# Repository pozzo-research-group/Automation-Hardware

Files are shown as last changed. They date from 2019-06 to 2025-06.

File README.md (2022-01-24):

# Custom Hardware for Automation
Pozzo Group Custom Automation Hardware. Dimensions are consistent with SLAS standards (slas.org) 

## Purpose
A place to store and share files for custom hardware and labware created for the laboratory automation including use with Opentrons pippetting robot and other tools. 

## Required Components
1. Any files (.stl, .dxf, etc.) necessary to create the hardware (3D printing, machining, laser cutting, etc.) 
2. Any drawings or description that is necessary to define the labware in liquid handling platforms (e.g. [Opentrons](https://support.opentrons.com/en/articles/3136504-creating-custom-labware-definitions))
3. Any additional instructions for printing, loading, or using the hardware



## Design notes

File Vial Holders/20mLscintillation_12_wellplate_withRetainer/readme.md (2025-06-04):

# 12 well 20mL vial holders
                                                                                                                                                                                                                                                            Works with 20mL scintillation vials. Use M3 heat set inserts in the holes on the well plate, and long m3 screws through the lids, to retain the vials in the well plate while withdrawing from septa.

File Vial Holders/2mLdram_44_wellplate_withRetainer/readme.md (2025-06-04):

# 44 well 2mL vial holders

Works with 2mL snap-top dram vials. Use M3 heat set inserts in the holes on the well plate, and long m3 screws through the lids, to retain the vials in the well plate while withdrawing from septa.

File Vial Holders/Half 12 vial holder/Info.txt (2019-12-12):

### Purpose
This holder can be used to hold twelve (12) 20 mL scintillation vials in a single
slot of the OT2 pipetting robot

### Use specifics
In order to make a single holder, two of these .stl files will need to be printed,
they then wedge together in a single slot holder and can hold 12 vials

### Measurements per 1 print
* Height:19.5 mm
* Length:85.87 mm
* Width: 63.85 mm
* Wells: 6
* Well Depth: 17.21 mm
* Well Diameter: 27.85 mm

### Well layout
[[A1 A2 A3 A4],
[B1 B2 B3 B4],
[C1 C2 C3 C4],

### Well Pipetting Order:
[A1, B1, C1, A2, B2, C2, A3, B3, C3, A4, B4, C4]

### Code for loading

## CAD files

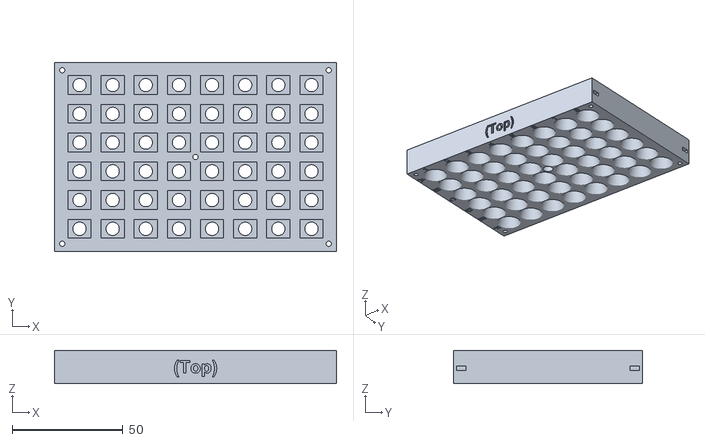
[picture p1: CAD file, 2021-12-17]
Cartridge Sample Holder for SAS Experiments/SAXS-USAXS 48 solid film holder/USAXS solid film holder cartridge v14 part 2.stl
127.5 x 85.5 x 15.0

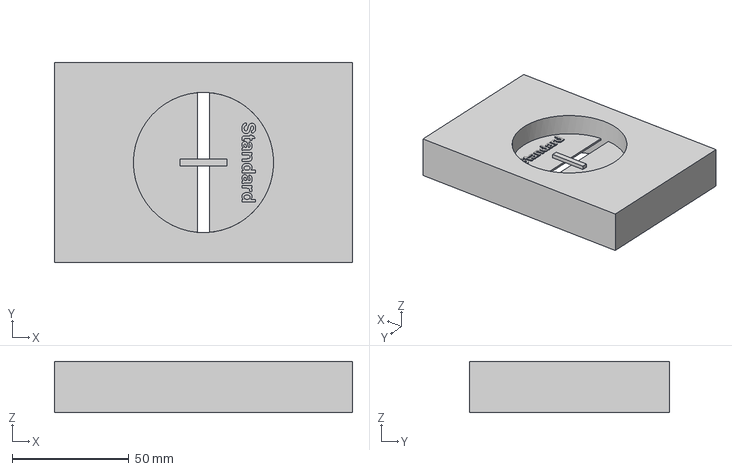
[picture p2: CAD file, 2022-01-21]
Cartridge Sample Holder for SAS Experiments/SAXS-USAXS calibrant holder/USAXS Calibrant Holder.step
127.5 x 85.5 x 22.0 mm

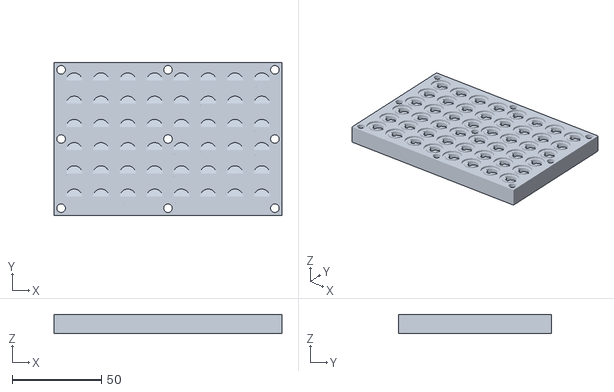
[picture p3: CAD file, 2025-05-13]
Cartridge Sample Holder for SAS Experiments/SAXS-USAXS Liquids 48 well plate holder/Sedimentation_wellplate.stl
127.6 x 85.5 x 10.9

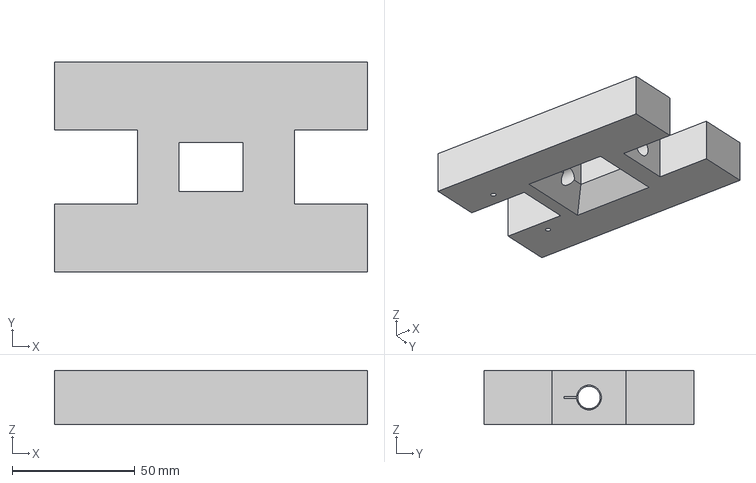
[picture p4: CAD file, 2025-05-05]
Cartridge Sample Holder for SAS Experiments/SAXS-USAXS_AntonPaar_FlowCellHolder/USAXS_flow cell holder v5.step
127.5 x 85.5 x 22.0 mm

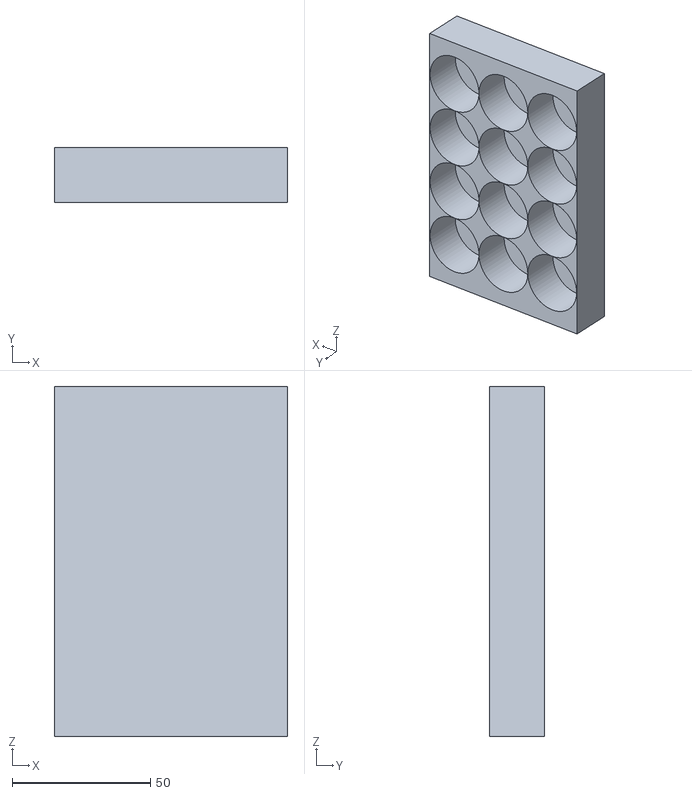
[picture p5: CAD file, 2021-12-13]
Vial Holders/20mlscintillation_12_wellplate_18000ul/20mlscintillation_12_wellplate_18000ul.stl
84.5 x 20.0 x 126.8

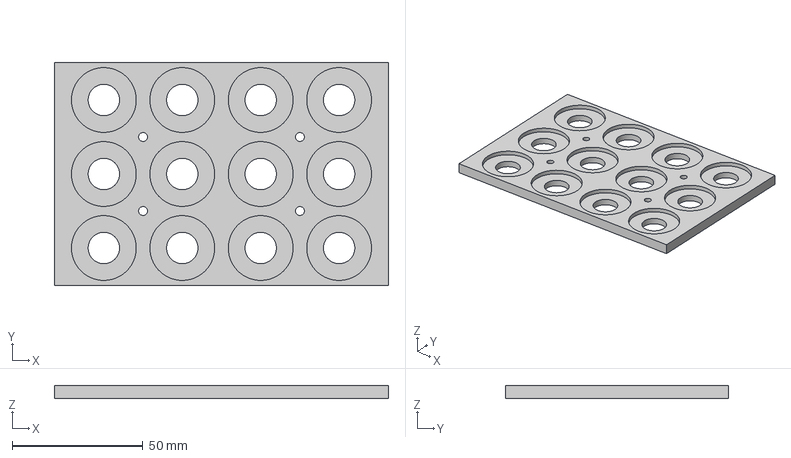
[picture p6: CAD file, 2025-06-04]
Vial Holders/20mLscintillation_12_wellplate_withRetainer/20cc_vial_plate_retainerlid v2.step
127.8 x 85.5 x 5.00 mm

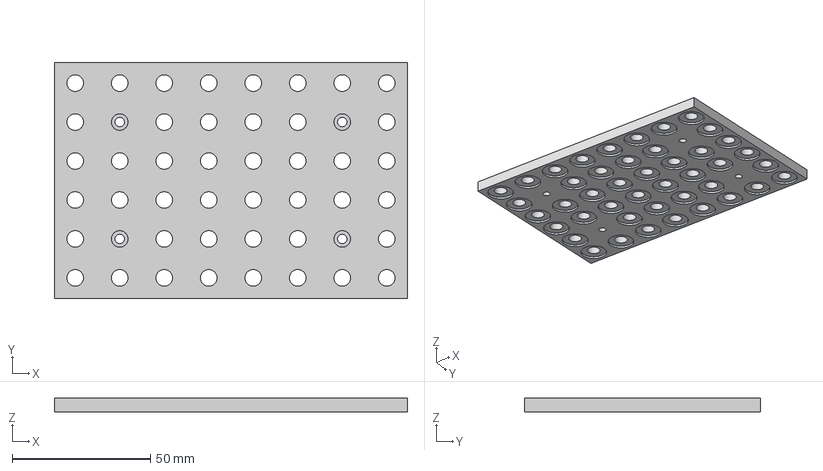
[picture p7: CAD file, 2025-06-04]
Vial Holders/2mLdram_44_wellplate_withRetainer/48_vial_plate_retainerLid v2.step
127.8 x 85.5 x 5.00 mm

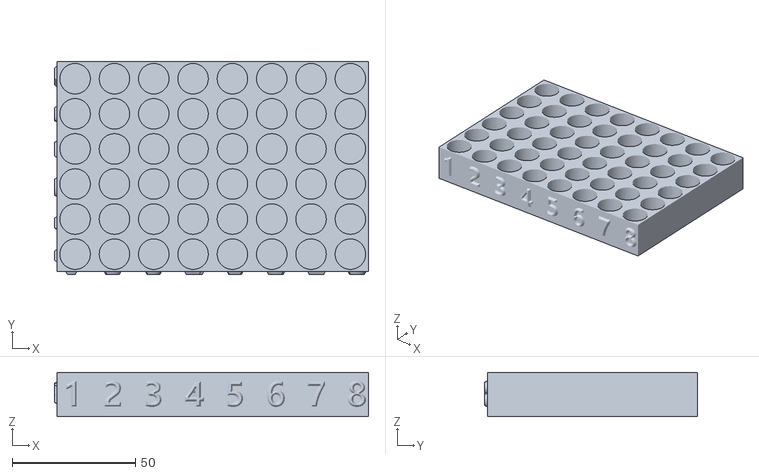
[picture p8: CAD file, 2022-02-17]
Vial Holders/48_well_vial_new_embossed.stl
127.5 x 86.7 x 18.0

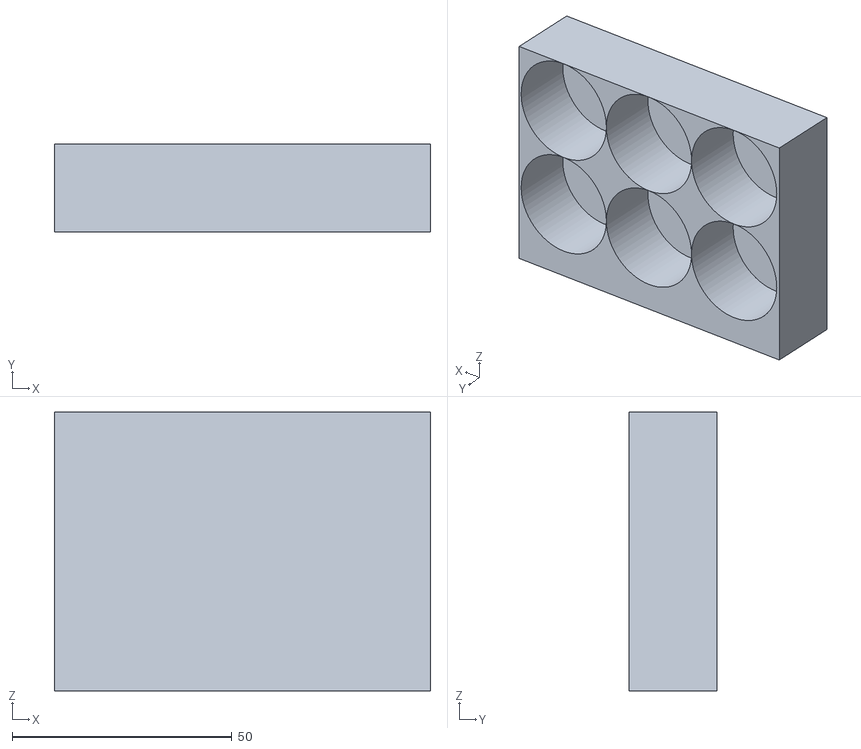
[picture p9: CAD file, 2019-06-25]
Vial Holders/Half 12 vial holder/Half 12 vial holder new.stl
85.5 x 20.0 x 63.4

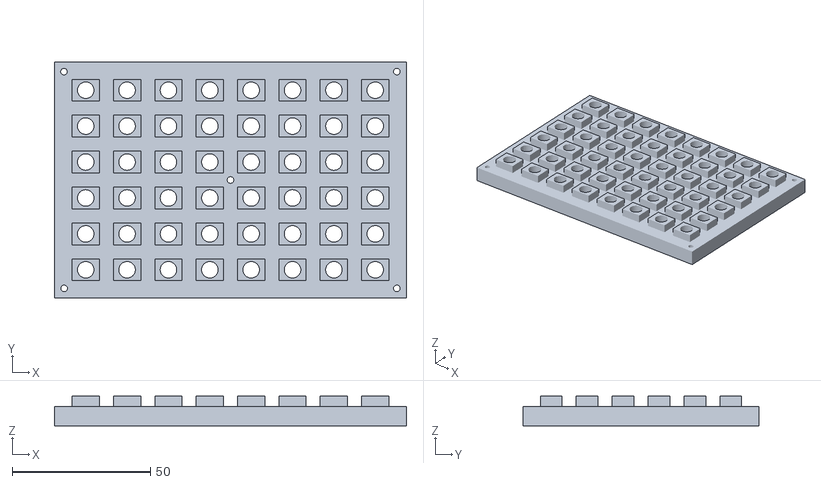
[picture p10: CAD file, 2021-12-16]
Cartridge Sample Holder for SAS Experiments/SAXS-USAXS 48 solid film holder/USAXS solids back (0p3mm gap).stl
127.5 x 85.5 x 10.7

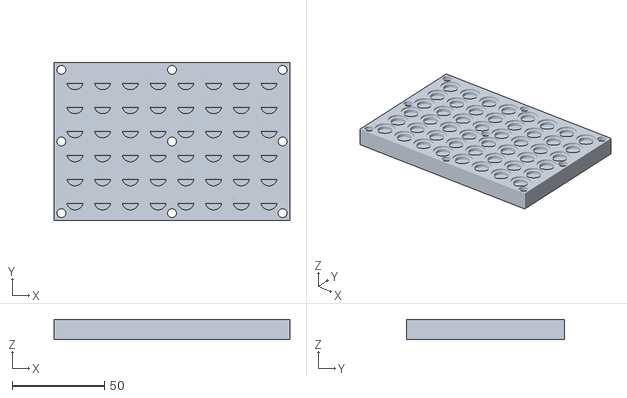
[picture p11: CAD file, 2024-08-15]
Cartridge Sample Holder for SAS Experiments/SAXS-USAXS Liquids 48 well plate holder/SAXS_2mm_sample_thickness - 48 Well (Center).stl
127.6 x 85.5 x 10.9

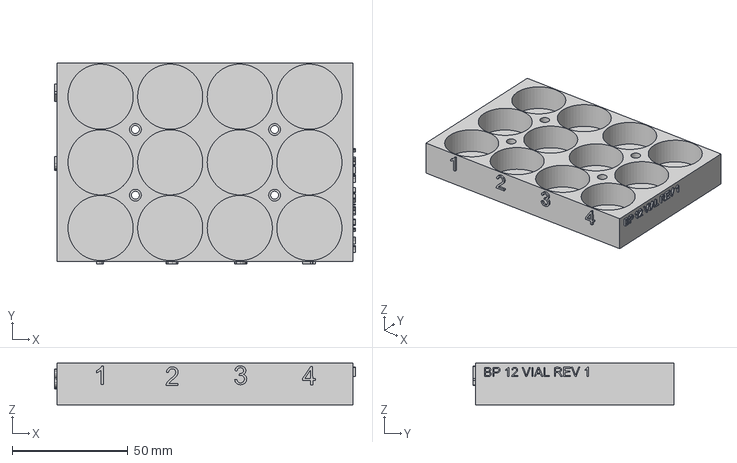
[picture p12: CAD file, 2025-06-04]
Vial Holders/20mLscintillation_12_wellplate_withRetainer/20cc_vial_plate v5.step
129.8 x 86.5 x 18.0 mm

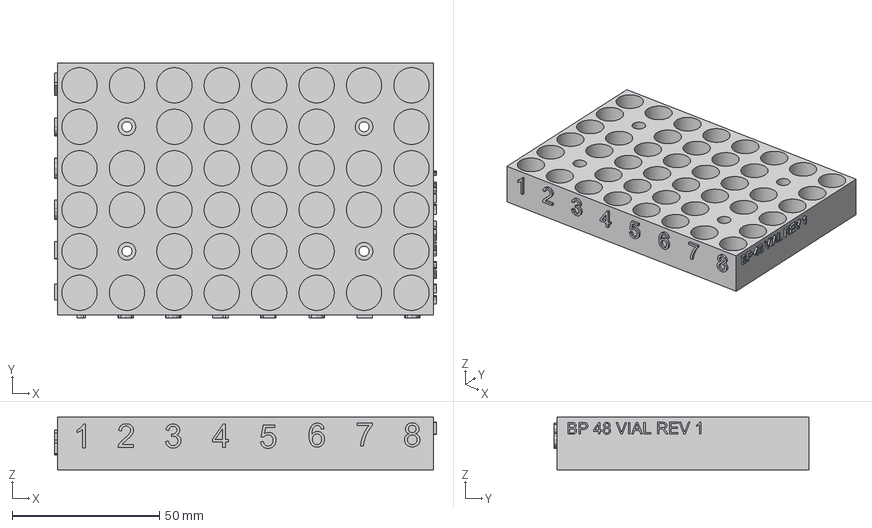
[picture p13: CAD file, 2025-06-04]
Vial Holders/2mLdram_44_wellplate_withRetainer/48_vial_plate v2.step
129.8 x 86.5 x 18.0 mm

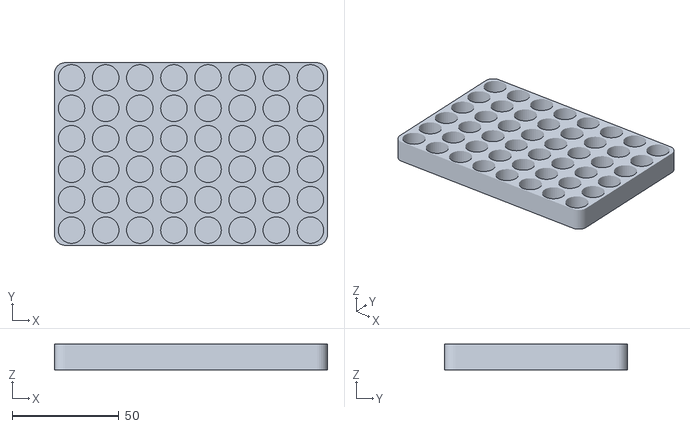
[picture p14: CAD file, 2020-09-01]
Vial Holders/48_well_2ml_vials.stl
127.8 x 85.5 x 12.0

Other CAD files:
Cartridge Sample Holder for SAS Experiments/SAXS-USAXS 48 solid film holder/USAXS solid back (0p8mm gap).stl
Cartridge Sample Holder for SAS Experiments/SAXS-USAXS Liquids 48 well plate holder/Cover plate detector - 48 Well USAXS.step
Cartridge Sample Holder for SAS Experiments/SAXS-USAXS Liquids 48 well plate holder/Cover Plate source - 48 Well USAXS.step
Cartridge Sample Holder for SAS Experiments/SAXS-USAXS Liquids 48 well plate holder/Center - 48 Well Liquids USAXS.step
Cartridge Sample Holder for SAS Experiments/SAXS-USAXS Liquids 48 well plate holder/KaptonWindow.dxf
Cartridge Sample Holder for SAS Experiments/SAXS-USAXS Liquids 48 well plate holder/USAXS liquid side unlabelled.stl
Cartridge Sample Holder for SAS Experiments/SAXS-USAXS Liquids 48 well plate holder/liquids center (aluminum insert).stl
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

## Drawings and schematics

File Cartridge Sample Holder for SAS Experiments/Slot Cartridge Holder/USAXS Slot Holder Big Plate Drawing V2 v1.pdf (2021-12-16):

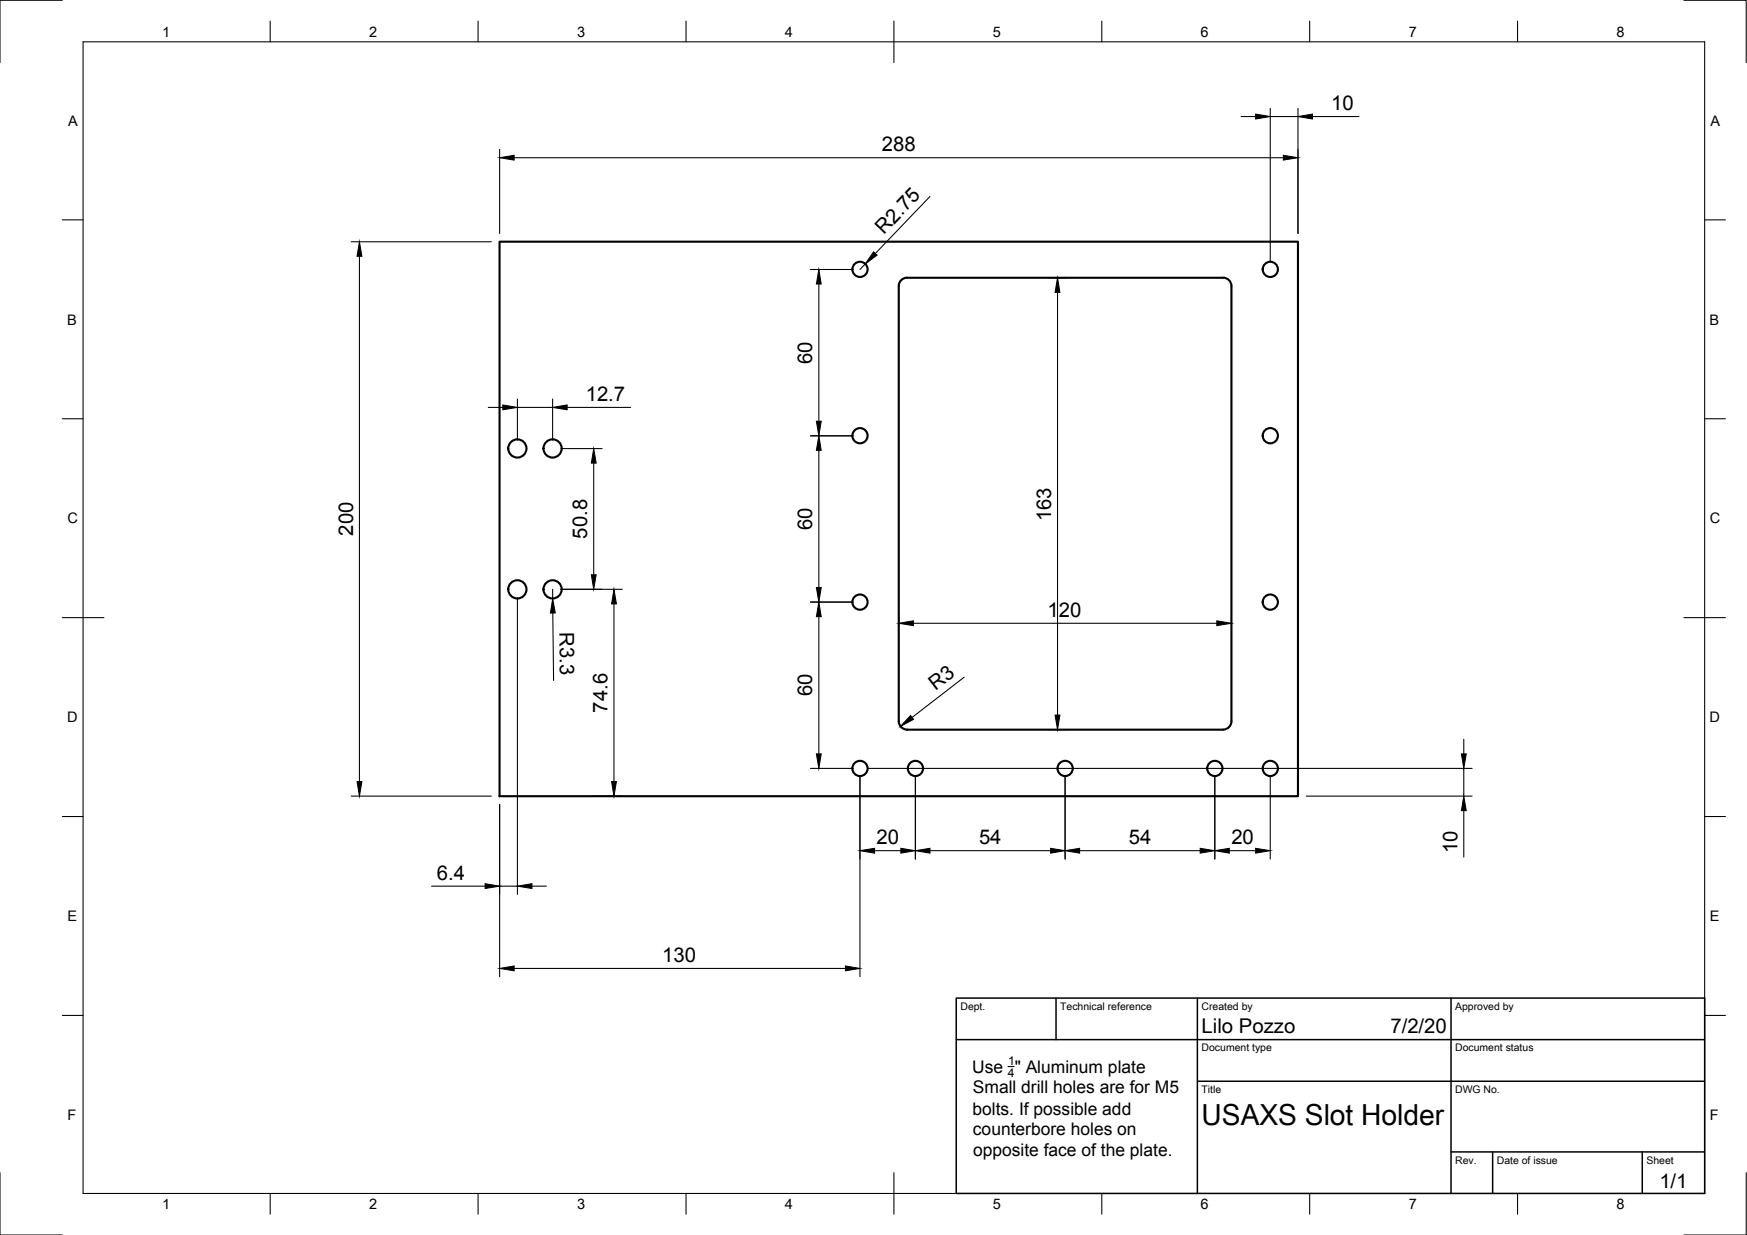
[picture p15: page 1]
Lilo Pozzo 200

Dept. | Technical reference | Created by 7/2/20 | Approved by

Use 1 " Aluminum plate 4 Small drill holes are for M5 bolts. If possible add counterbore holes on opposite face of the plate. | | Document type | Document status

Title USAXS Slot Holder | DWG No.

Rev. | Date of issue | Sheet 1/1

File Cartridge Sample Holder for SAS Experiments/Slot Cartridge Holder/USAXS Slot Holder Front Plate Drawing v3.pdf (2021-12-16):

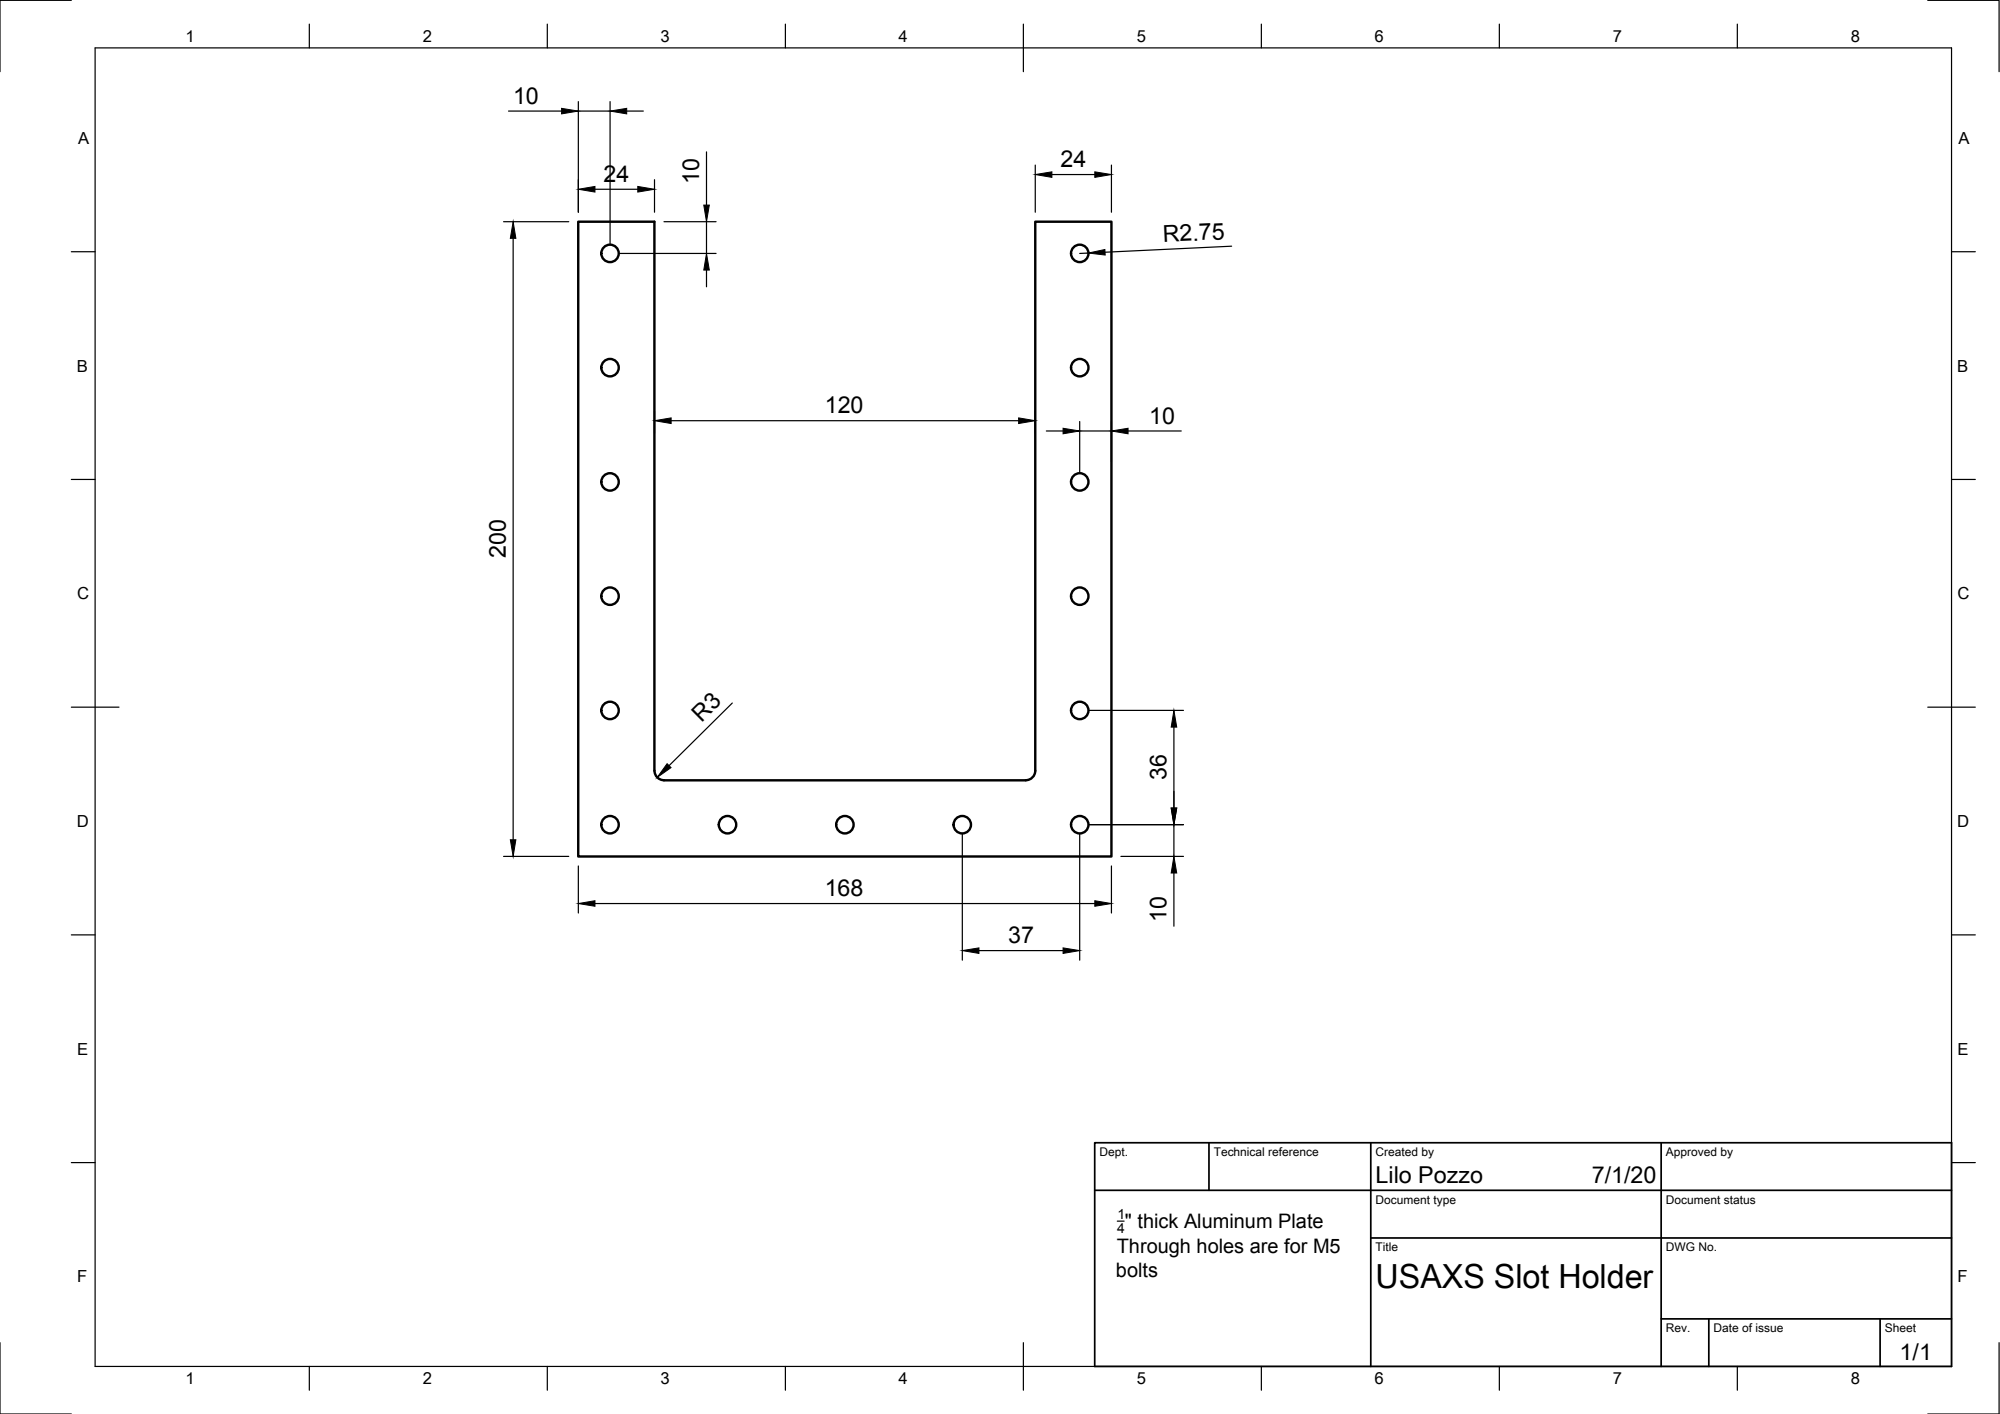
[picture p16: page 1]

Dept. | Technical reference | Created by Lilo Pozzo 7/1/20 | Approved by

1/4" thick Aluminum Plate Through holes are for M5 bolts | | Document type | Document status

Title USAXS Slot Holder | DWG No.

Rev. | Date of issue | Sheet 1/1

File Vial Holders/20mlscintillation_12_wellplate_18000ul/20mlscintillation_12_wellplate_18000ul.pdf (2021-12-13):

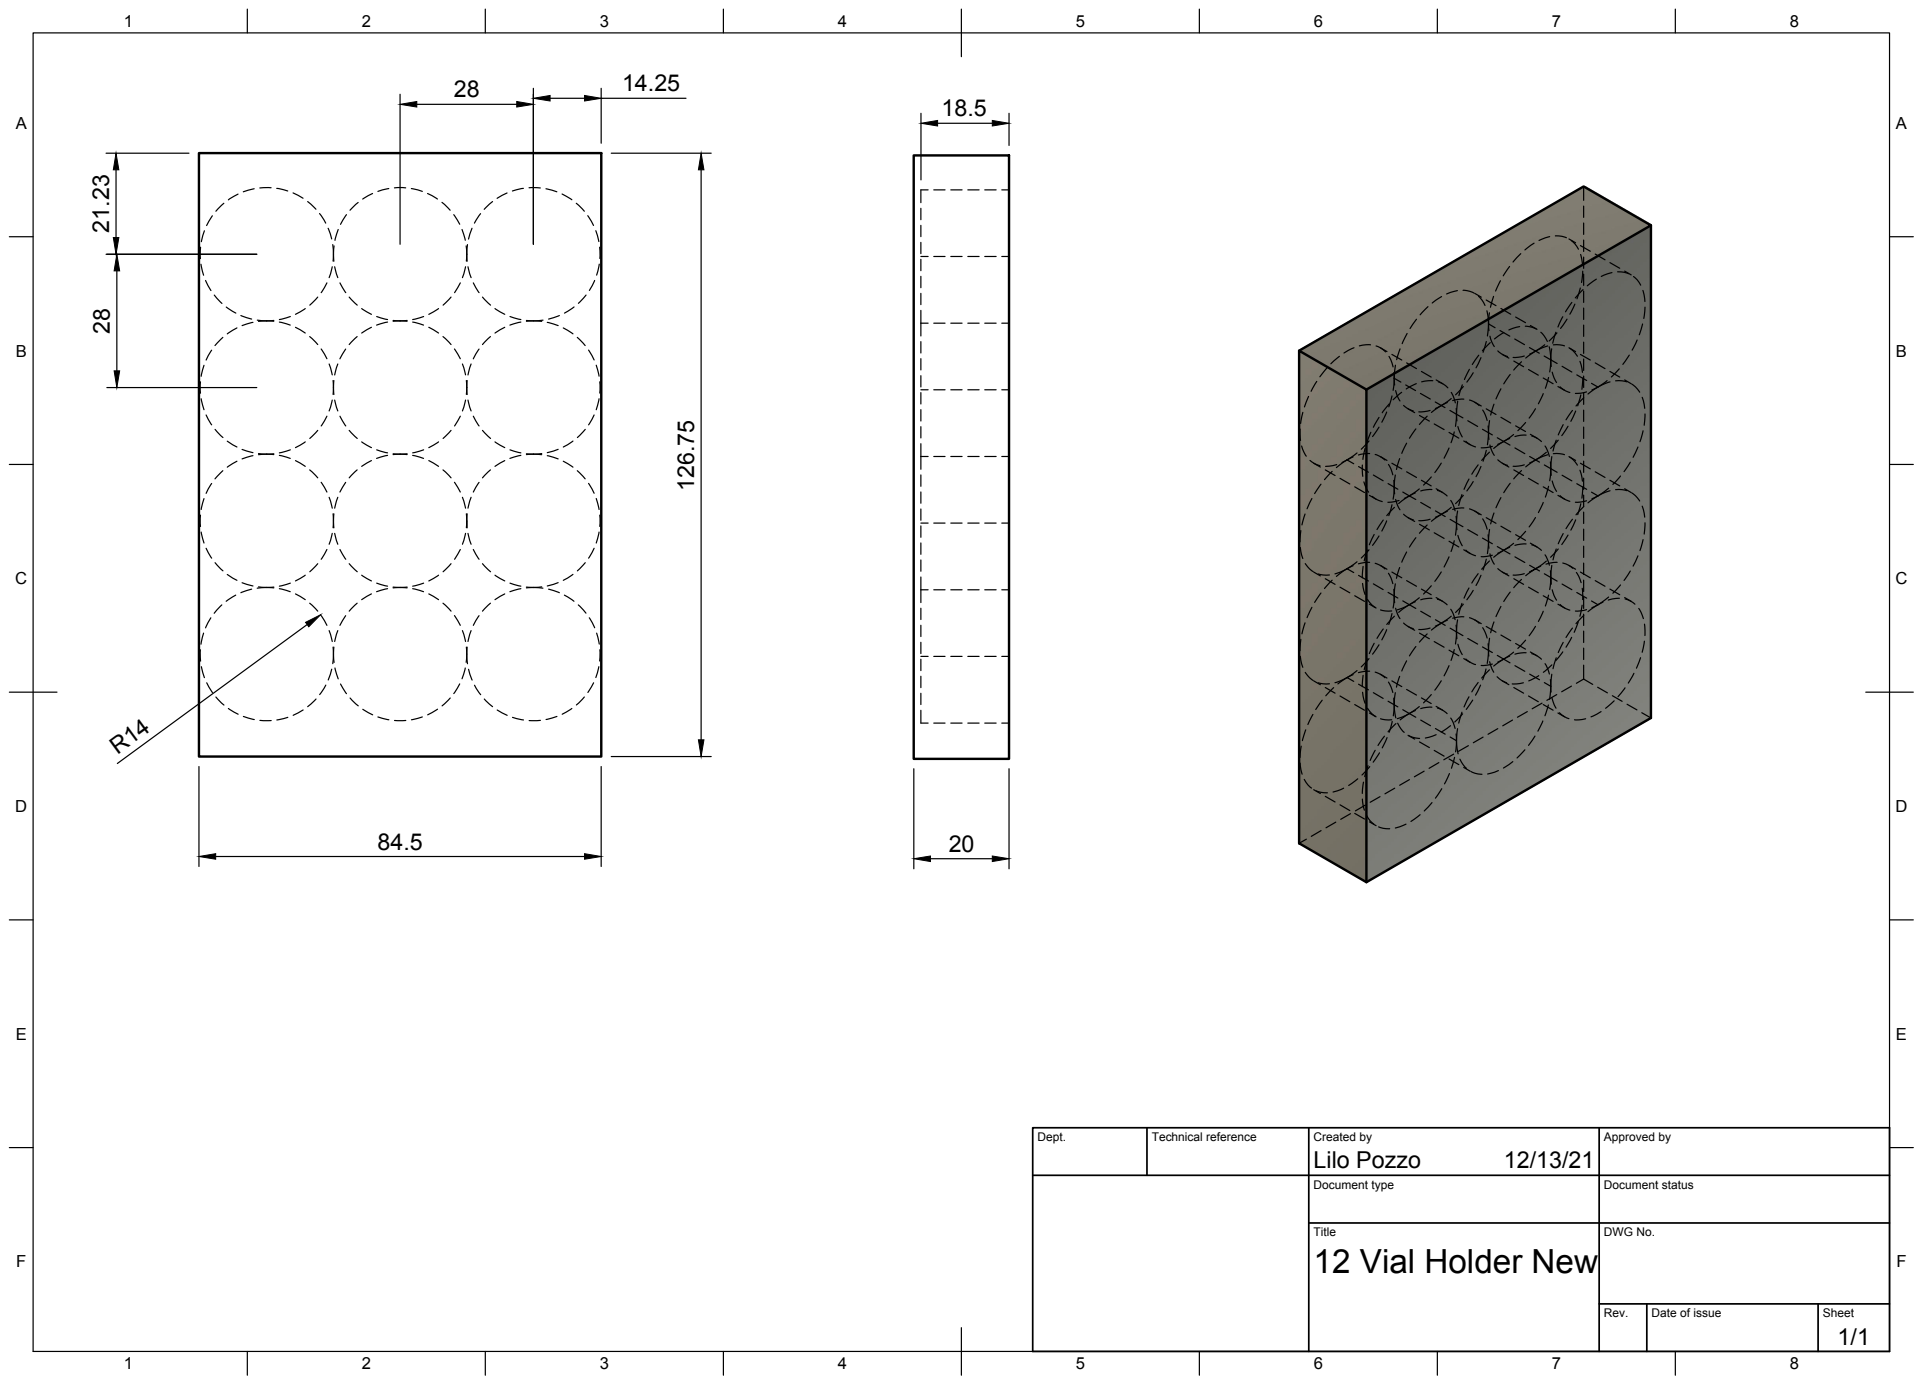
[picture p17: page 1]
Title; DWG No.; Rev.; Date of issue; Sheet

Dept. | Technical reference | Created by Lilo Pozzo 12/13/21 | Approved by

Document type | Document status

12 Vial Holder New

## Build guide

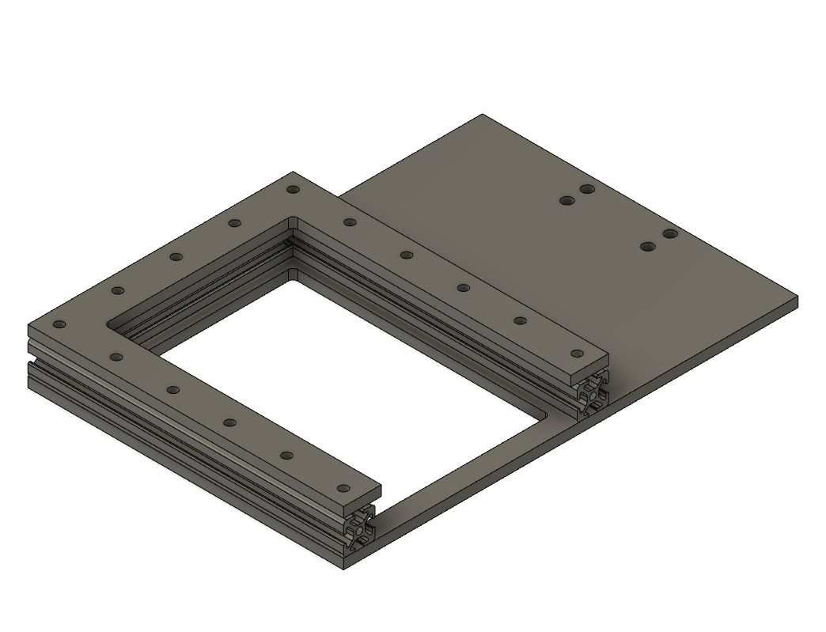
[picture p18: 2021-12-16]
Cartridge Sample Holder for SAS Experiments/Slot Cartridge Holder/USAXS Slot Holder Assembly v6 2.png

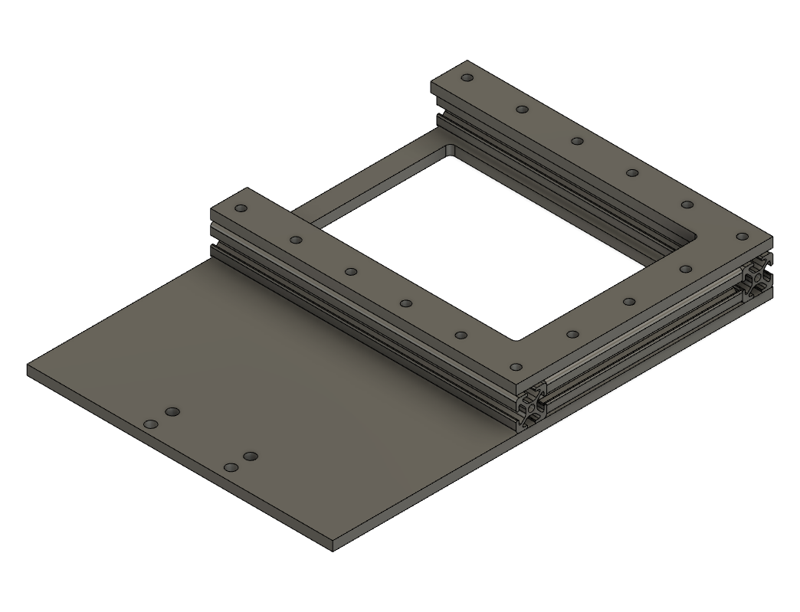
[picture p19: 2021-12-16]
Cartridge Sample Holder for SAS Experiments/Slot Cartridge Holder/USAXS Slot Holder Assembly v6.png

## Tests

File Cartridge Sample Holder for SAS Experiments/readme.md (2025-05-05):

A variety of sample holder designs for use with SAXS cartridge stages. The Slot Cartridge Holder is a cartridge stage adapter for use at APS USAXS 12-ID-E to mount a cartridge cell to the instrument's sample stage. It is constructed out of aluminum plate and extrusion. Use it to mount the solid, liquid, or flow cell holders. The calibrant is used to hold a standard. Tape the standard onto the side of the holder with the 'nub' sticking out.

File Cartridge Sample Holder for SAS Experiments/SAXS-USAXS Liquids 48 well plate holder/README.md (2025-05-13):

# List of Materials

| Supplier      | Material and Dimensions                      | Catalog Number                 | Part Name              | Qty. |
|---------------|----------------------------------------------|--------------------------------|------------------------|------|
| Formlabs      | Clear or Gray                                | RS-F2-GPCL-04 or RS-F2-GPGR-04 | Center piece/main body | 1    |
| McMaster-Carr | Aluminum                                     | 9140T109                       | Cover plate source     | 1    |
| McMaster-Carr | Aluminum                                     | 9140T109                       | Cover plate detector   | 1    |
| McMaster-Carr | Kapton (0.0010" thick)                       | 2271K401                       | Windows                | 2    |
| McMaster-Carr | Buna-N or EPDM (1.5 mm wide, 9 mm ID)        | 9262K126 or 1289N319           | O-rings                | 96   |
| McMaster-Carr | Stainless steel M3 (8 mm Long, 0.5 mm Pitch) | 90666A104                      | Screws                 | 18   |
| MiSUMi        | Brass Cadmium-Free (M3x0.5 mm)               | FB-305580                      | Threaded insert        | 9    |
| McMaster-Carr | Moisture-Resistant Polyester Film (Mylar)    | 8567K102                       | Windows                | 1    |

# Assembly Instructions

For the USAXS 48-wellplate (1cm sample thickness) 
  1. Insert o-rings into center piece face which will be facing the X-ray source.
  2. Place Kapton sheet and then the aluminum cover piece which will be facing the source on top of the o-rings.
  3. Insert screws and fasten in the order specified in the image.
  4. Turn over the plate and insert o-rings.
  5. Load liquid samples manually or with a liquid-handling system. Suggested volume is 450 μL.
  6. Place second Kapton sheet and aluminum cover plate on top, and fasten using the same order of screws.

For the SAXS_2mm_sample_thickness - 48 Well (2mm sample thickness) or Sedimentation_wellplate
  1. Start with the backside of the plate (which will be facing the beam)
  2. Place the aluminum cover on the plate and fasten with screws 
  3. Flip the plate over and insert o-rings
  4. Load liquid samples manually or with a liquid-handling system. Suggested volume is 200 μL.
  5. Place Kapton or Mylar sheet and then the aluminum cover piece on top of the o-rings.
  6. Insert screws and fasten in the order specified in the image.

<figure>
Trulli
<figcaption align = "center"><b>Left, step by step assembly instructions; right, cartridge holder seated in slot cartridge holder frame along with calibrant holder cartridge.</b></figcaption>
</figure>

<br/><br/>

<figure>
Trulli
<figcaption align = "center"><b>Cartridge holder has the same dimensions as a standard well plate and may therefore be used in liquid handling platforms, such as the OT-2 pictured here. </b></figcaption>
</figure>

## Misc.
- Alternative file formats are available upon request. 
- We have had issues with new batches of o-rings not fitting in the center piece despite ordering the same part number and using the same files and procedure for 3D printing the center piece. Future revision to the O-ring source or the size of the O-ring grooves is pending. 
- Testing for leaks between wells and out of the cartridge itself is essential. We recommend filling wells with an alternating pattern of water and water with food dye added to help identify problematic areas.

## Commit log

2019-06-25 Add files via upload
    This is a holder for 6 x 20 mL Scintillation Vials. Two of these will fit into an OT2 slot allowing for 12 vials per slot. STL file is ready for slicing for 3D printing.
    [Half 12 vial holder new.stl]
2019-12-12 Adding text file with some information about the print as well as some measurements
2019-12-12 moving the vial holder to separate folders
    [Half 12 vial holder new.stl]
2019-12-12 deleting extra file
    [Half 12 vial holder new.stl]
2021-12-13 add new labware
    [20mlscintillation_12_wellplate_18000ul.stl]
2021-12-16 Add files via upload
    Added STL files for 48 solid film holder. These can now be printed with any 3D printer. It needs more documentation to show necessary size of machine screws and square nut inserts for full assembly.
    [USAXS solid back (0p8mm gap).stl, USAXS solids back (0p3mm gap).stl]
2021-12-16 Add files via upload
    Added STL Files for middle spacer and side plates (tapered cone version) for the liquid 48 well cartridge cell. It is recommended to machine the side-plates out of aluminum or similar to add stiffnes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
    [USAXS liquid side unlabelled.stl, liquids center (aluminum insert).stl, liquids holder middle (aluminum) #11.stl]
2021-12-16 Add files via upload
    Add drawing for simple ambient temperature slot holder. Assembly should be straightforward using 2020 extrusion aluminum cut to size and associated M5 bolts, nuts.
2022-01-13 Added a .dxf that will help with cutting out kapton on a laser cutter
    [KaptonWindow.dxf]
2022-01-21 Changed directory layout
    [KaptonWindow.dxf, USAXS liquid side unlabelled.stl, USAXS solid back (0p8mm gap).stl, USAXS solid film holder cartridge v14 part 2.stl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]
2022-01-21 Added new cartridge style holder files
    [Center - 48 Well Liquids USAXS.step, Cover Plate 1 - 48 Well Plate USAXS.step]
2022-01-21 Added more .stp files
    [Cover Plate source - 48 Well USAXS.step, Cover plate detector - 48 Well USAXS.step, USAXS Calibration Holder.step]
2022-01-21 Moved files
    [20mlscintillation_12_wellplate_18000ul.stl, 48_well_2ml_vials.stl, Half 12 vial holder new.stl]
2022-01-24 Moved calibrant holder out of liquids dir
    [USAXS Calibrant Holder.step]
2022-02-14 Added opentrons files for USAXS liquid sample holder
2022-02-17 resin 48 well plate
    [48_well_vial_new_embossed.stl]
2024-08-15 update README for instructions on SAXS 2mm Wellplate
2024-08-15 add .stl file for the SAXS 2mm thickness wellplate
    [SAXS_2mm_sample_thickness - 48 Well (Center).stl]
2025-05-05 add flow cell holder
    [USAXS_flow cell holder v5.f3d, USAXS_flow cell holder v5.step, USAXS_flow cell holder v5.stl]
2025-05-13 add files for sedimentation measurments
    [Sedimentation_wellplate.stl]
2025-06-04 add 2mL and 20mL well plates with retainers
    [20cc_vial_plate v5.f3d, 20cc_vial_plate v5.step, 20cc_vial_plate v5.stl, 20cc_vial_plate_retainerlid v2.f3d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]
